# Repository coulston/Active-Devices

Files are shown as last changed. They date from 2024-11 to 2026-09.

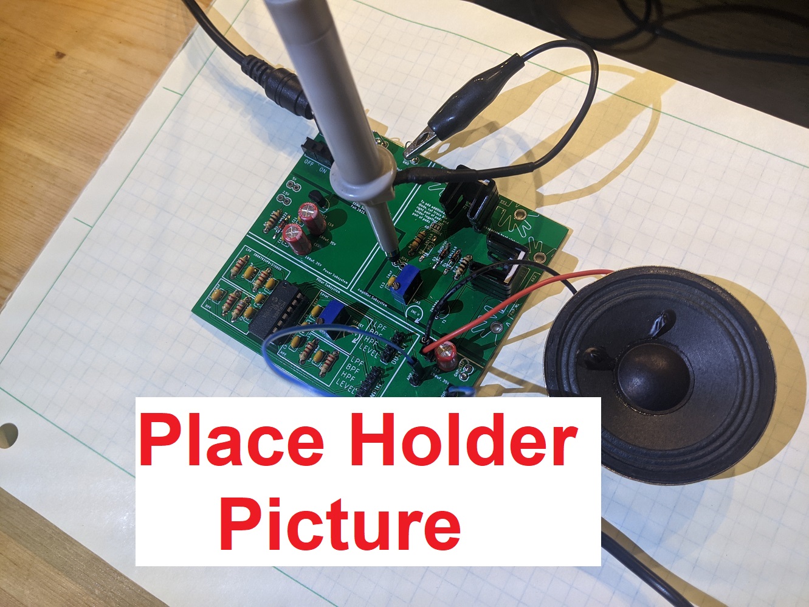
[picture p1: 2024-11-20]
Labs/lab22 audio amplifierMeasurement/img/placeHolderPicture.jpg

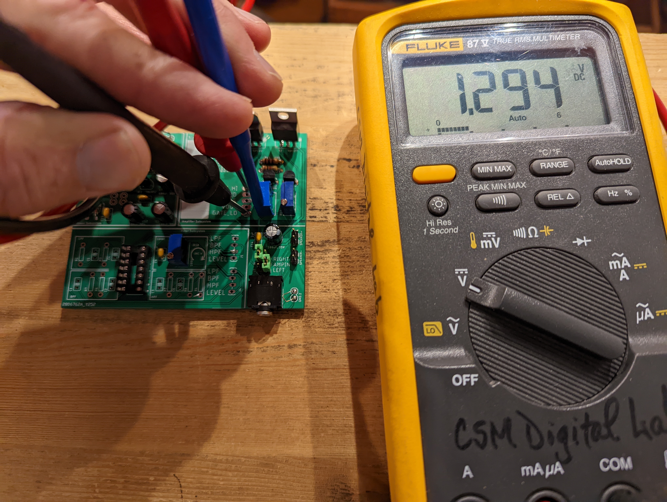
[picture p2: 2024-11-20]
Labs/lab22 audio amplifierMeasurement/img/adjustMultiplierVoltage.jpg

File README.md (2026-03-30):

Here is a set of resources that I've developed while a faculty member at the Colorado School of Mines.  These resources come in two flavors:

## Laboratories

The labs presented here require students to predict circuit behavior using circuit theory, simulate the circuit, and then build the circuit.  The first two
sets of labs below require multiple lab session to complete, showing students how combine building block circuits to produce complex behavior.
* The design/test/assembly of a BJT curve tracer on a custom PCB.  Based on w2aew's design presented on this [YouTube](https://www.youtube.com/watch?v=ZOLLoa2fH24) video.
* The design/test/assembly of an audio amplifier and audio frequency filters on a custom PCB.
* The analysis of a prebuilt, fully analog, PID controller.
* The analysis of a prebuilt full-bridge Rectifier/Buck converter.

## Workbook
I remember working problems from Schaums outline series as an undergraduate.  Working a long series of similar but distinct circuit
problems helped me hone my skill.  Most textbooks have a small set of problems to work; a volume that did not consistently produce
mastery in my students.  So I spent a summer writing the circuit problems that you will find here.  This is a work in progress and
I would certianly apprecaite any suggestions for problems to add.

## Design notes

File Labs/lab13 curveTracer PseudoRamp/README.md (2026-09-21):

# BJT Curve Tracer - Lab 4 The Pseudo Ramp Generator

This is the fourth in a series of junior year Electrical Enineering laboratories aimed at building a BJT curve tracer. 
In this lab you will analyze, simulate and assemble a Pseudo Ramp Generator that will build an almost linear ramp 
waveform with the help of the 555 Timer and Schmitt Trigger Relaxation Oscillator.  As you work you way through
the lab you will learn how to:
* Use a software tool to perform time domain analysis of an electronic circuit.
*	Analyze and design a circuit containing resistors and op amps.
*	Analyze and design a circuit consisting of several building blocks.
* Assemble a circuit on a PCB.
* Use test and measurement equipment to analyze electronic circuits.

This curve tracer is based on the YouTuber w2aew video 
[#232: More Circuit Fun: Simple transistor curve tracer using Stairstep generator circuit](https://www.youtube.com/watch?v=ZOLLoa2fH24). 
The hardware for this series of labs is located in this repo, [here](https://github.com/coulston/Active-Devices/tree/main/curveTracerResources).
Click the video below to be taken to a video overview of this laboratory.

YouTube (https://www.youtube.com/watch?v=ZmqhOJkoOfk)
  
All this material is avaible under CC BY-NC-SA 4.0

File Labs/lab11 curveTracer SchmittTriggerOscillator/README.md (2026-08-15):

# BJT Curve Tracer - Lab 2 The Schmitt Trigger Relaxation Oscillator

This is the second in a series of junior year Electrical Enineering laboratories aimed at building a BJT curve tracer. 
In this lab you will analyze, simulate and assemble a Schmitt Trigger Relaxation Oscillator that generates a low duty-cycle 
squarewave that will be an integral subsystem in the curve tracer circuit.  As you work you way through the lab you will learn how to:
* Use a software tool to perform time domain analysis of an electronic circuit.
*	Analyze and design a circuit containing resistors and op amps.
* Assemble a circuit on a PCB.
* Use test and measurement equipment to analyze electronic circuits.

This curve tracer is based on the YouTuber w2aew video 
[#232: More Circuit Fun: Simple transistor curve tracer using Stairstep generator circuit](https://www.youtube.com/watch?v=ZOLLoa2fH24). 
The hardware for this series of labs is located in this repo, [here](https://github.com/coulston/Active-Devices/tree/main/curveTracerResources).
Click the video below to be taken to a video overview of this laboratory.

YouTube (https://www.youtube.com/watch?v=oDtQ2bS_qQ8)

All this material is avaible under CC BY-NC-SA 4.0

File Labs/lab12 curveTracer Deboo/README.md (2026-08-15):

# BJT Curve Tracer - Lab 3 The Deboo Integrator

This is the third in a series of laboratories aimed at building a BJT curve tracer.  In this lab you will
analyze, simulate and assemble a circuit based on the classic 555 timer that generates a low duty-cycle
squarewave that will be an integral subsystem in the curve tracer circuit.  As you work you way through
the lab you will learn how to:
* Use a software tool to perform time domain analysis of an electronic circuit.
*	Analyze and design a circuit containing resistors and op amps.
* Assemble a circuit on a PCB.
* Use test and measurement equipment to analyze electronic circuits.

This curve tracer is based on the YouTuber w2aew video 
[#232: More Circuit Fun: Simple transistor curve tracer using Stairstep generator circuit](https://www.youtube.com/watch?v=ZOLLoa2fH24). 
The hardware for this series of labs is located in this repo, [here](https://github.com/coulston/Active-Devices/tree/main/curveTracerResources).
Click the video below to be taken to a video overview of this laboratory.

YouTube (https://www.youtube.com/watch?v=O_E52ka0kKk)

All this material is avaible under CC BY-NC-SA 4.0

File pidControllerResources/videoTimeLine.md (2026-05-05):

Overview Video

<start with graphic of PID Controller Board>

**Introduction**

For the past 10 years I've been teaching a Feedback and Control of Dynamic

Systems class at the Colorado School of Mines.  This class covers a wide variety 

of concepts and links them together.  What the class lacks is a way of creating 

a hands-on understanding of the concepts presented in class.

\*Hello, my name is Christopher Coulston and I'd like to introduce you to the 

the analog PID Controller created to address this problem.

**What is a Feedback Controller?**

In order to build a feedback controller you need something that you want to control.

We call this the plant.

<add evolving graphic, plant, ref input, error, controller>

You need to provide the feedback controller the value that you want the output to have.  This is

called the reference input.

The feedback controller computes the difference of the reference input and the plant output. This

is called the error of the system.

The error, its integral and derivative are added together creating the control signal. 

This control signal is sent as input to the plant.

The PID Controller board allows measurement of these values at a set of headers along the 

top of the board.

**Goals of the Feedback Controller**

When I started this project I had the following goals:

Physically Robust:  Students are hard on equipment and any mechanical interface is bound to break.

Inexpensive:

Made from discrete components:  I wanted student to see how simple electronic building blocks

can be assembled to form complex functionality.

Use jelly bean parts: You should be able to source the parts from many different vendors.

Flexible: Should allow users to test a variety of concepts presented in a from feedback control course.

Open Source: Please copy and adapt this work to your needs.

**The Analog PID Controller**

Let's look at the analog PID Controller.

<add graphic showing PID Controller PCB>

The headers at the top of the board provide access to all the signals in a feedback controller.

The reference input to the PID Controller comes from one of three sources:

* A push button
* A potentiometer
* An external function generator

You select the reference source by moving this jumper.

You can observe the output of the PID Controller using an oscilloscope.

The behavior of the PID Controller is determined by the PID gains, set by the three 

potentiometers.

**Using the Analog PID Controller**

Let's setup the analog PID Controller board.  This will require

* Split power supply.  A pair of 9V battery's will work fine.
* A 2-channel oscilloscope
* Optional function generator

Set up the power supply, +9V, GND and -9V

Configure and connect the function generator

Attach the output to the oscilloscope

Start tuning...

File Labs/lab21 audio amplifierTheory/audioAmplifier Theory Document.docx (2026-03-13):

EENG 385 - Electronic Devices and Circuits

Audio Board: Amplifier Theory

Lab Handout

# Outcome and Objectives

The outcome of this lab is to determine the input resistance, gain, and output resistance of the two stages in the audio amplifier. Through this process you will achieve the following learning objectives:

- Perform a DC and AC analysis of a circuit containing BJT.
- Analyze and design a circuit containing one or more BJTs.
- Analyze and design a circuit consisting of several building blocks.

# Audio Amplifier

The heart of the Audio Amplifier is shown in the schematic shown in Figure 1. In the analysis that follows, you will set VCC to 9V.

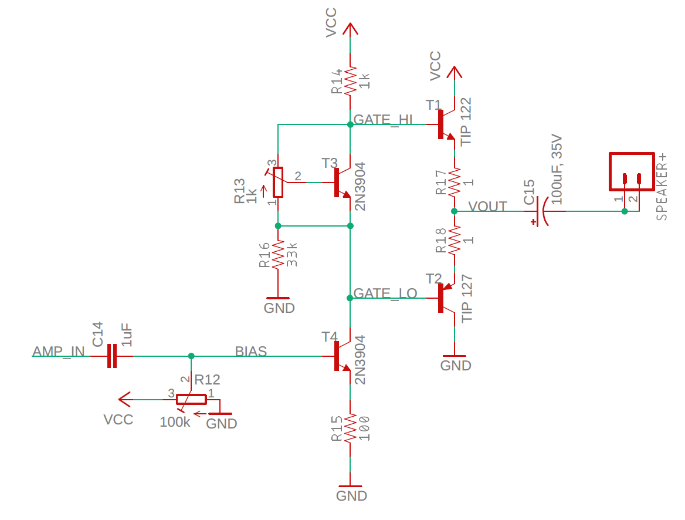
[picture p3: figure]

Figure 1: The core of the audio amplifier consists of a voltage gain stage followed by a current gain stage. Some artistic modifications have been made to the original schematic.

The output stage consists of a pair transistor/resistor pairs T1/R17 and T2/R18.

You are to treat the 1Ω resistors R17/R18, connected to the emitters of T1/T2 respectively, as 0Ω resistors. Hence, they are ignored in the rest of the following analysis. While these resistors do not play an important role in the signal amplification, these emitter degeneration resistors provide negative feedback in the output stage, helping to prevent thermal runaway.

These two output transistors are each in a common collector configuration. In the configuration shown in Figure 1:

- The base of T1 is 0.7V above the emitter.
- The base of T2 is 0.7V below the emitter

When an NPN and PNP transistor are arranged as shown in Figure 1, they are said to form a push/pull pair. The term alludes to the manner in which the pair pull the speaker towards VCC or push it towards GND. When we analyze the individual transistors in the push/pull pair, we will refer to them as emitter followers. The output of the push/pull pair should be centered at Vcc/2 = 4.5V so that the output voltage can swing as far as possible before hitting either rail.

Compute the emitter follower base voltages as follows:

1) In order for the output of the push/pull pair be 4.5V, what should you set the base voltage of transistor T1 to?
2) In order for the output of the push/pull pair be 4.5V, what should you set the base voltage of transistor T2 to?
3) What is the voltage difference between the voltages found in Questions 1 and 2?

# Common Emitter Theory

Transistor T3 in Figure 2 is configured as a common emitter. The base of T3 is the input and the collector is the output. Both the input and output voltages are measured with respect to the emitter terminal. Thus, the emitter is in common with both the base and the collector.

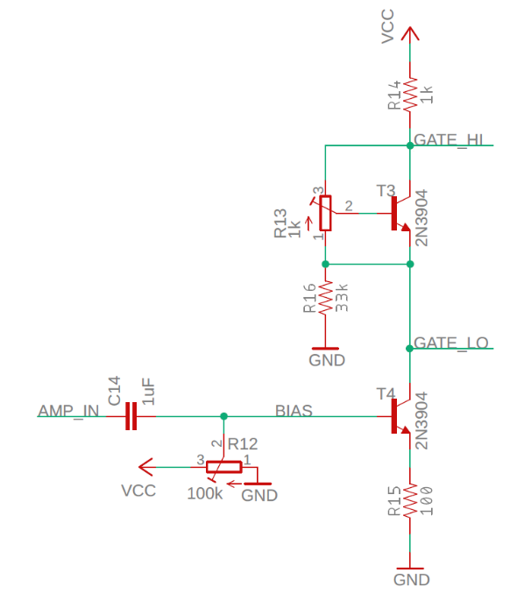
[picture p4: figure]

Figure 2: The common emitter stage of the audio amplifier.

The AMP_IN signal in Figure 2 comes from our audio source. Capacitor C14 removes the DC component from the audio signal and passes along an AC signal centered at 0V. The audio signal output of the capacitor is added (via superposition) to the bias voltage supplied by the potentiometer. You need to adjust the bias voltage so that the bases of the push/pull pair are set to the voltages you calculated in Questions 1 and 2 above. In other words, in the absence of an AC signal source, you need to:

- Set GATE_LO to 3.8V.
- Set GATE_HI to 5.2V.

Now you will use this information to adjust the bias voltage of the common emitter stage. Compute the common emitter bias voltage as follows:

1) Find the current through R14 so that GATE_HI is 5.2V where VCC = 9V.

You’ll explore the function of transistor T3 in the next section, but for the time being assume T3 is in the active mode, so IC = IE. Furthermore, assume that a negligible amount of emitter current from T3 runs through R16. Hence all the current through the resistor R14 runs into the collector of T4.

2) Find VE for T4 assuming that IE is equal to IC.
3) Find VB for T4 (your value should be close 1V).

# The Vbe Multiplier

The preceding section should have made it clear that the base of the two output transistors T1 and T2 in Figure 1 need to be 1.4V apart. This function is performed by the transistor T3, resistor R16 and the potentiometer R1 shown at left in Figure 3.

In order to make your analysis easier, ignore resistor R16. We can do this because the current flowing through R16 is 10 times smaller than the current flowing through R13. Hence, by KCL, 90% of the current flowing through R13 flows back to the emitter of T3, shown at right in Figure 3.

This circuit is called a Vbe multiplier for reasons that we will now explore.

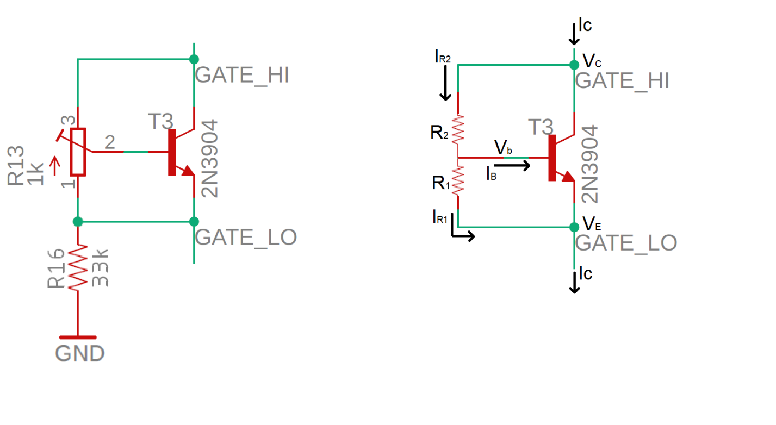
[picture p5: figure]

Figure 3: (left) The Vbe multiplier circuit used in our Audio amplifier. (right) The circuit used in the analysis.

Look at the left circuit Figure 3; adjusting the potentiometer R13 moves the center tap of the potentiometer along a 1kΩ track of resistive carbon film connecting terminals 1,3. If the center tap is moved closer to terminal 1 then the resistance between terminals 1,2 decreases and the resistance between terminals 2,3 increases. Thus, the sum of the resistance between terminals 1,2 plus the resistance between terminals 2,3 adds to 1kΩ. You will use the circuit shown in the right side of Figure 3 to analyze the Vbe multiplier. Note that the potentiometer is replaced with a pair of resistors so that R1 + R2 = 1kΩ.

1. From the previous section, what is the current IC?

Assume that the BJT in Figure 3 is in the active region and that ß = 100,

2. What is IB for this value of IC?
3. Write an equation for the current IR1 in terms of VBE and R1.
4. Assume that the center tap of the potentiometer is halfway so that R1 = R2 and VBE = 0.7V. What is the current IR1 equal to?
5. In this case, how much larger is IR1 than IB? Compute this as the ratio IR1/IB.
6. Write a KCL equation for the VB node.
7. Since IR1 is a lot larger than IB, rewrite this KCL assuming that IB = 0.
8. Write an equation for VCB in terms of IR2 and R2.
9. Replace the IR2 term in the previous step with the equation in step 3
10. Write an equation for VCE in terms of VCB and VBE.
11. Replace the VCB term in the previous step using the equation in part 9
12. Factor out the VBE term in the previous step.

This final equation shows that VCE is VBE times some factor. In other words, VBE is multiplied by a factor to get VCE. Hence the name, Vbe multiplier.

Now let’s dig into the amplifier using the framework shown in Figure 4. This figure is an abstract version of Figure 1 for small AC signals. It describes how the signal is mathematically manipulated. The Source is the audio input that you are providing.

The blue area labeled Common Emitter in Figure 4 is the circuit shown in Figure 2. Let’s look at this stage in the overall circuit shown in Figure 1. The input to this stage, Vce is the voltage at the base of transistor T4 in Figure 1, the BIAS test point on the PCB. The output of the Common Emitter stage is the collector of transistor T4 in Figure 1, the GATE_LO test point.

The blue area labeled Emitter Follower in Figure 4 is the circuit shown in Figure 6. Let’s look at this stage in the overall circuit shown in Figure 1. The input to this stage, Vef, is the voltage at the base of transistor T2 in Figure 1, the GATE_LO test point. The output from this stage is the emitter of transistor T2 in Figure 1, the VOUT test point.

Some of you may have wondered why include resistor R16 at all? R16 is included in Figure 2 so that there is always a path for current to flow through the biasing potentiometer R13 regardless what the amplifier is doing.

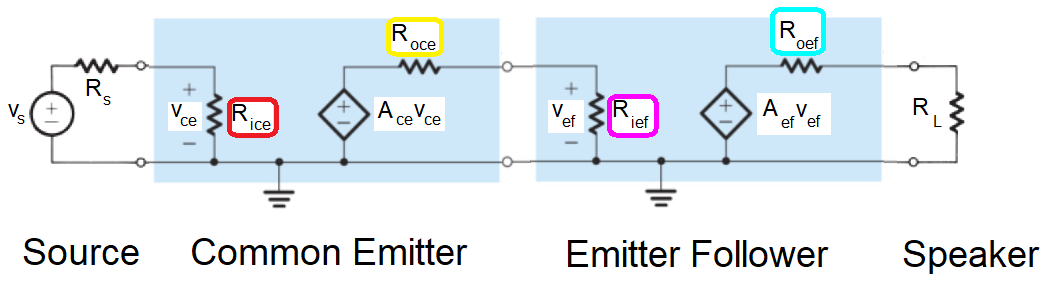
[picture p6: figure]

Figure 4: The small signal model of the Audio board. The input signal goes through a common emitter to amplify the voltage and then into an emitter follower to amplify the current before being sent out to the speakers.

Your task is to assign equations and values to the variables in Figure 4 and put them into Table 1. This information is critical in understanding how to improve the quality of the audio output.

Table 1: Model parameters for the cascade amplifier shown in Figure 4.

| Rin | Rout | Voltage Gain
Source | N/A | Rs = 10Ω | N/A
Common Emitter | Rice = | Roce = | Ace =
Emitter Follower | Rief = | Roef = | Aef =
Speaker | RL = 8Ω

Let’s start by analyzing the common emitter amplifier from Figure 2, but in the more reduced form shown in Figure 5. Note the Vbe multiplier has been remove from Figure 2 and replaced by a wire. This is an acceptable substitution because we are interested in the behavior of the common emitter BJT, not the Vbe multiplier.

In this analysis you are frequently going to be asked to find the change in voltage of a node. A change in a voltage is not the same thing as the value of the voltage. For example, if I asked you to describe the relationship between the change in the emitter voltage (ΔVE ) in Figure 5 and the change in emitter current (ΔIE), you could use Ohm’s law to write:

ΔVE = R ΔIE

If you were then asked to solve this equation for ΔIE, you would write:

ΔIE = ΔVE/R

The steps in the derivations are numbers. Occasionally you will need to use an equation derived in a previous step to move the derivation forwards. When doing this, look for equivalent variables in the two steps, you will probably either substitute one equation into another or set two equations equal.

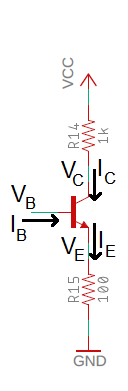
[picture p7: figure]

Figure 5: A simplified version of the common emitter shown in Figure 2.

Compute the input impedance of the common emitter stage - Rice. You will need to reference Figure 5 during this analysis.

1) What is the relationship between ΔVB and ΔVE?
2) Use Ohm’s law to describe the relationship between ΔVE and ΔIE.
3) Solve the previous equation for ΔIE and replace ΔVE with ΔVB from step 1.
4) Write down the relationship between ΔIE and ΔIB? (Hint, it is a bad parameter.)
5) Equate the equations from step 3 and 4 using ΔIE.
6) Solve equation from step 5 for ΔVB / ΔIB, this is the input impedance of the common emitter. Insert this value into the Rice cell of Table 1.

Compute the output impedance of the common emitter stage - Roce. You will need to reference Figure 5 during this analysis.

1) Use Ohm’s law to describe the relationship between ΔVC and ΔIC.
2) Solve Equation 1 for ΔVC/ΔIC. This value is the output impedance of the common emitter. Insert this value into the Roce cell of Table 1.

Compute the gain of the common emitter stage - Ace. You will need to reference Figure 2 during this analysis.

1) What is the relationship between ΔVB and ΔVE?
2) Use Ohm’s law to describe the relationship between ΔVE and ΔIE.
3) Solve the previous equation for ΔIE.
4) Replace ΔVE in the equation from step 3 with the relationship found in the equation from step 1.
5) Use Ohm’s law to describe the relationship between ΔVC and ΔIC. Note the sign!
6) Since ΔIE = ΔIC, replace ΔIC in the previous step with ΔIE.
7) Substitute ΔIE from the equation in step 4 into the equation from step 6.
8) Let ΔVC/ΔVB, be the gain. What is the gain of our amplifier? Insert this value into the Ace cell of Table 1.

# Emitter Follower Theory

We now return our attention to the cascade amplifier of Figure 4 and fill in the Table 1. We will focus on the push/pull output stage formed by a pair of emitter followers. I’ve made some changes to the push/pull circuit shown in Figure 1 to produce the circuit shown in Figure 6.

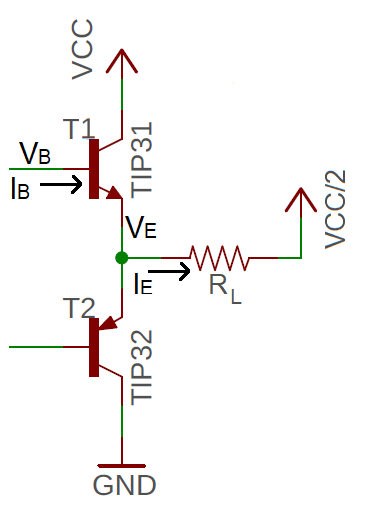
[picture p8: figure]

Figure 6: The output stage of the audio amplifier consists of a pair of emitter followers.

I made the changes going from Figure 1 to Figure 6. These changes are valid and made to simplify the analysis. For example, since this is a small signal analysis (we are looking at changes in values e.g. ΔVB) we will ignore the 100uF capacitor C13 in Figure 6 because the capacitor appears as a short at audio-frequencies. The speaker is rated as an 8Ω load, represented by RL – please use RL in the subsequent analysis. Finally, focus on the labeled NPN transistor, T1, in Figure 6 when answering the following questions.

Compute the input impedance of the emitter follower - Rief. You will need to reference Figure 6 during this analysis.

1) What is the relationship between ΔVB and ΔVE?
2) Use Ohm’s law to describe the relationship between ΔVE and ΔIE. Call the resistance of the speaker RL.
3) Solve the previous equation for ΔIE and replace ΔVE with ΔVB (using the relationship in equation 1)
4) What is the relationship between ΔIE and ΔIB? Hint, it involves a bad parameter.
5) Equate the equations from steps 3 and 4 using ΔIE.
6) Solve equation in step 5 for ΔVB/ΔIB, this is the input impedance of the emitter follower. Insert this value into the Rief cell of Table 1.

Compute the output impedance of the emitter follower – Roef. You will need to reference Figure 6 during this analysis.

1) Use Ohm’s law to describe the relationship between ΔVE and ΔIE. Call the resistance of the speaker RL.
2) Solve the equation from step 1 for ΔVE/ΔIE, this is the output impedance of the emitter follower. Insert this value into the Roef cell of Table 1.

Compute the voltage gain of the emitter follower - Aef. You will need to reference Figure 6 during this analysis.

1) What is the relationship between ΔVB and ΔVE?
2) Solve the equation from step 1 for ΔVE/ΔVB, this is the voltage gain of the emitter follower. Insert this value into the Aef cell of Table 1.

Compute the overall gain of amplifier with no load:

Since our analysis will break down if we do not have a load resistance, we will model an open circuit output as a 1MΩ resistor as shown in Figure 7. In this analysis assume a value of β =100.

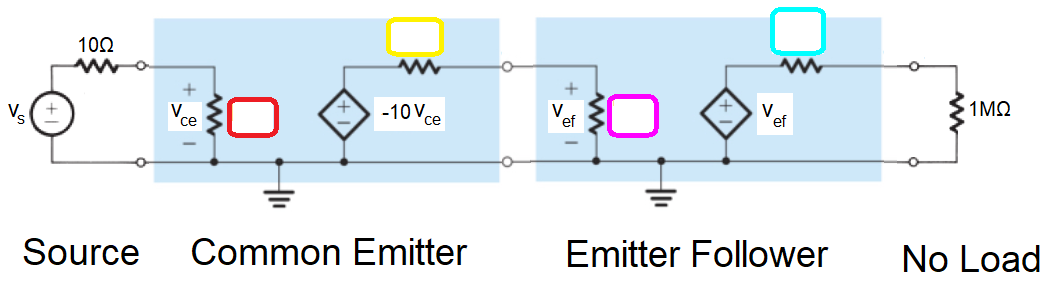
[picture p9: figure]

Figure 7: The Audio amplifier with a very high load resistance that models no load.

1. Fill in the values of the resistors shown in Figure 7.
2. Compute Vce in terms of Vs. Use this to determine the gain Vce/Vs. Assume 20,000 + 10 = 20,0000.
3. Compute Vef in terms of Vs. Use this to determine the gain Vef/Vs. Assume 200,000,000 +1,000 = 200,000,000
4. Calculate the current delivered to the 1MΩ load. Assume that 1/1,000,000 = 0.

Analysis of amplifier with 8Ω load

We will model the speaker as an 8Ω resistor as shown in Figure 7. In this analysis assume a value of β =100.

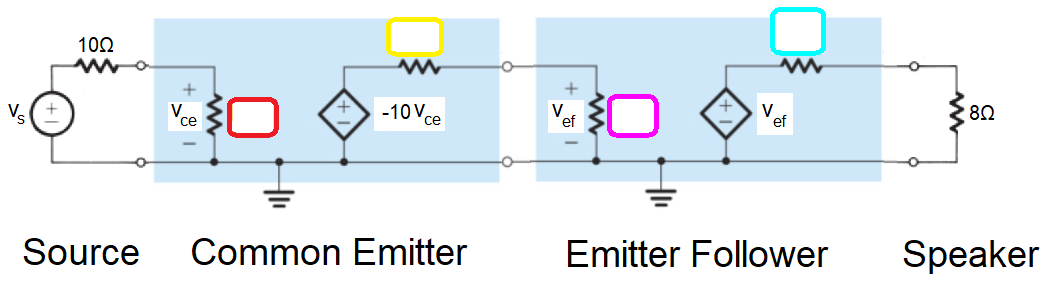
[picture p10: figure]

Figure 8: The Audio amplifier with an 8Ω load that represents a speaker.

1. Fill in the values of the resistors shown in Figure 8. Assume β =100.
2. Compute Vce in terms of Vs. Use this to determine the gain Vce/Vs. Assume 20,000 + 10 = 20,000.
3. Compute Vef in terms of Vs. Use this to determine the gain Vef/Vs.
4. Calculate the current delivered to the 8Ω load in terms of Vs.

# Assembly

This lab document does not contain any information of the assembly process. Please consult the Assembly Guide posted on Canvas for more information.

# Testing the Amplifier Subsystem

Until the pair of potentiometers are adjusted, your amplifier subsystem will not work properly. It would be best to have someone else check your component placement and orientations and check theirs. Then come to lab next week ready to learn how to adjust the potentiometers and get some sound from your amplifier.

# Turn In

Make a record of your response to numbered items below and turn them in a single copy as your team’s solution on Canvas using the instructions posted there. Include the names of both team members at the top of your solutions. Use complete English sentences to introduce what each of the following listed items (below) is and how it was derived.

Hint, use Ctrl+click to follow links. This also works for all the Figures and Tables in these labs.

Audio Amplifier

Steps 1 – 3

Common Emitter Theory

Steps 1 – 3

The Vbe Multiplier

Steps 1 – 12

Compute the input impedance of the common emitter stage - Rice.

Steps 1 – 6

Compute the output impedance of the common emitter stage - Roce.

Steps 1 – 2

Compute the gain of the common emitter stage - Ace.

Steps 1 – 8

Compute the input impedance of the emitter follower - Rief.

Steps 1 – 6

Compute the output impedance of the emitter follower – Roef.

Steps 1 – 2

Compute the voltage gain of the emitter follower - Aef.

Steps 1 – 2

Compute the overall gain of amplifier with no load

Steps 1 – 4

Compute the overall gain of amplifier with 8Ω load

Steps 1 – 4

Complete Table 1

Audio Board: Amplifier Theory

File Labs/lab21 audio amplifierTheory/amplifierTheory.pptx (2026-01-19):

## EENG 385 Amplifier Theory

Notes: Usually the <title of the lab> is what will be called the “System” through the rest of this document

## Lab Objectives

The objective of this lab is to analyze the operation and electrical characteristics of the audio amplifier stage of the Audio board and to prepare you to solder together the audio amplifier subsystem of the Audio board.

## Theory

Two stage
- Input from audio source via 3.5mm jack
- Common emitter, voltage amplifier
- Emitter follower, current amplifier

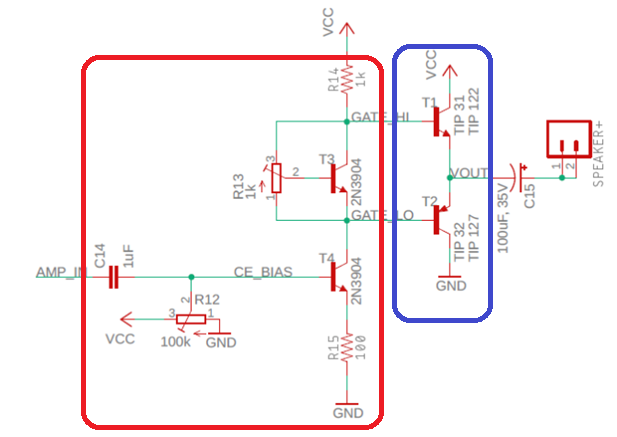
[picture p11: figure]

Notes: Replace <System> with the name of the

## Theory

- Model circuit with small signal model
- Vs is audio source, your MP3 player
- Use analysis to determine values in colored boxes


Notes: Replace <System> with the name of the

## Small Signal Input Resistance

- Small signal input resistance
  - Looks at changes in voltage/current
- Example: Find Rice
  - V = I*R so Rice = ΔvB / ΔiB
  - Effect of ΔvB on ΔvE at T4?
  - Effect of ΔiE on ΔvE at T4?
  - Relationship between ΔiB on ΔiE

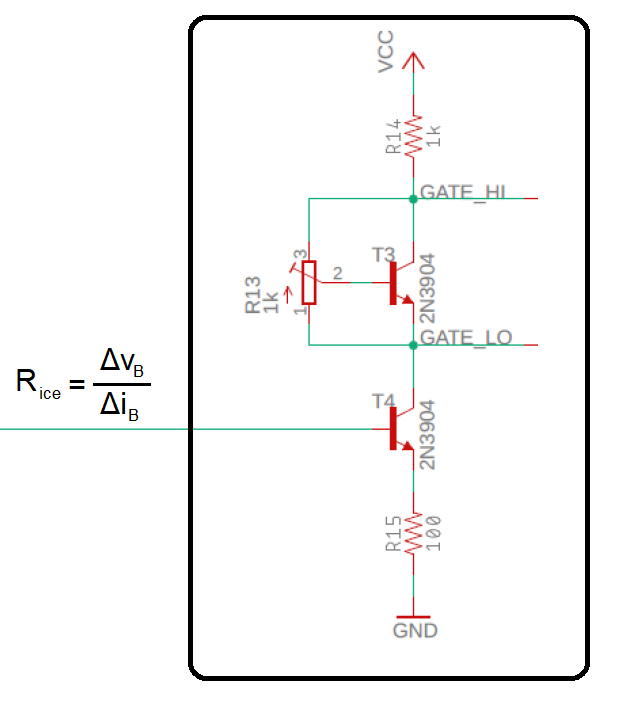
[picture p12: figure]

## Assemble

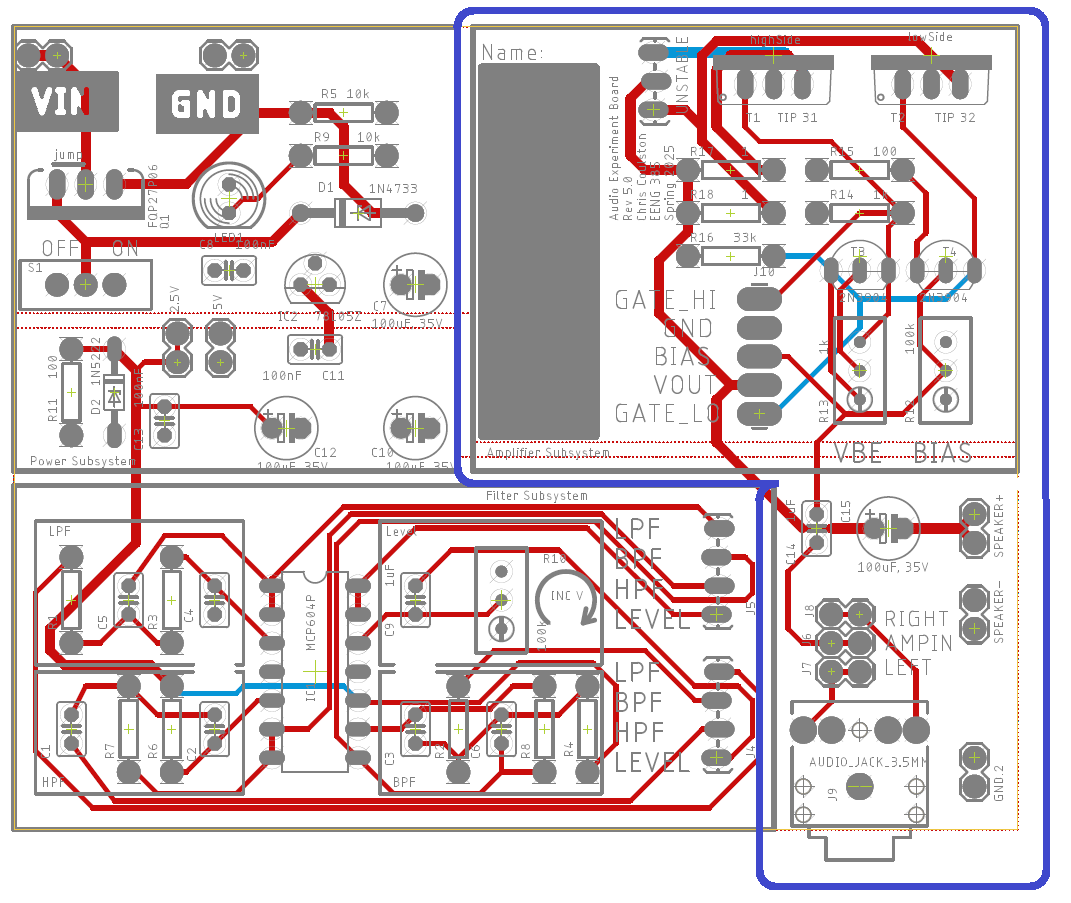
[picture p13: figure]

- Audio input & amplifier
- Polarized parts
  - 100uF
  - TIP 122 NPN
  - TIP 127 PNP
  - 2N3904
  - 1k and 100k Pot

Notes: Replace <System> with the name of the

## Test

- No testing of assembled circuit
  - If POTs are not adjusted, it may look like your circuit has a short circuit
  - Wait until next week’s lab to power up.

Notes: Replace <System> with the name of the

## Turn In

Audio Amplifier Steps 1 – 3
Common Emitter Theory Steps 1 – 3
The Vbe Multiplier Steps 1 – 12
Rice Steps 1 – 6
Roce Steps 1 – 2
Ace Steps 1 – 8
Rief Steps 1 – 6
Roef Steps 1 – 2
Aef Steps 1 – 2
Gain of amplifier with no load Steps 1 – 4
Gain of amplifier with 8Ω load Steps 1 – 4
Complete Table 1

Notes: Replace <System> with the name of the

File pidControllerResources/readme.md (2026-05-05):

# PID Controller

<image of PID Controller>

The PID Controller board is designed as a practical laboratory experience for students to understand how to characterize a plant, and tune a PID Controller.  Through this process you will achieve the following learning objectives:
* Analyze an opamp circuit that implements a PID controller and plant.
* Characterize a plant
  * Determine the transfer function of the plant
  * Determine the frequency reponse of the plant by building its Bode plot
  * Compute gain and phase margin of a plant by building its Nyquist plot
* Hands on tuning of a PID controller.

Video Title (https://www.youtube.com/watch?v=VIDEO_ID)

# Documentation
* [PID Laboratory](../Labs/lab50%20pidController/pidControllerLab.pdf)
* Videos
    * Overview
    * Characterizing the plant
* Hardware
    * PID Controller [Schematic](./pidControllerRev8schematic.pdf) and [Layout](./pidControllerRev8layout.pdf)
    * Source files to build your own
       * EAGLE CAD [Schematic](./manufacture/pidControllerRev8.sch) and [Layout](./manufacture/pidControllerRev8.brd)
       * [Gerber Files](./manufacture/pidControlRev8Gerber)
       * [Bill of Materials](./manufacture/pidControllerMaster_BOM.xlsx)
       * [Centroid File](./manufacture/pidController_Centroid.xlsx)

# Respository Contents

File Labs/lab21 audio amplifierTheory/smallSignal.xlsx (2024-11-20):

gm | 0.1181102362
 |  | Measure |  |  | Calculated
Freq | Volume Setting | Vb(ch1)pp | Ve(ch2)pp | Vc(pp) | Vbe(pp) | ic(pp) mA | Vc(pp) error
1kHz | 30 | 200 | 181 | 1.8 | 19 | 2.24 | 0.44
 | 40 | 265 | 240 | 2.4 | 25 | 2.95 | 0.55
 | 50 | 330 | 298 | 3 | 32 | 3.78 | 0.78
 | 60 | 393 | 355 | 3.5 | 38 | 4.49 | 0.99
 | 70 | 458 | 414 | 4.05 | 44 | 5.2 | 1.15
 | 80 | 523 | 469 | 4.59 | 54 | 6.38 | 1.79
 | 90 | 589 | 524 | 5.12 | 65 | 7.68 | 2.56
 | 100 | 652 | 572 | 5.56 | 80 | 9.45 | 3.89

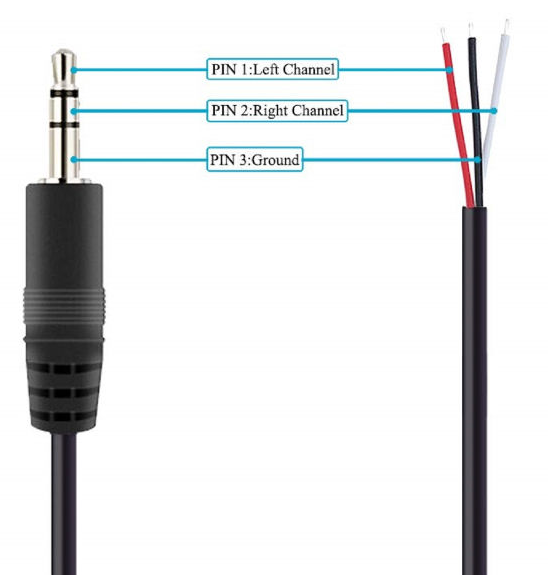
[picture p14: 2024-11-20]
Labs/lab21 audio amplifierTheory/img/audioCable.bmp

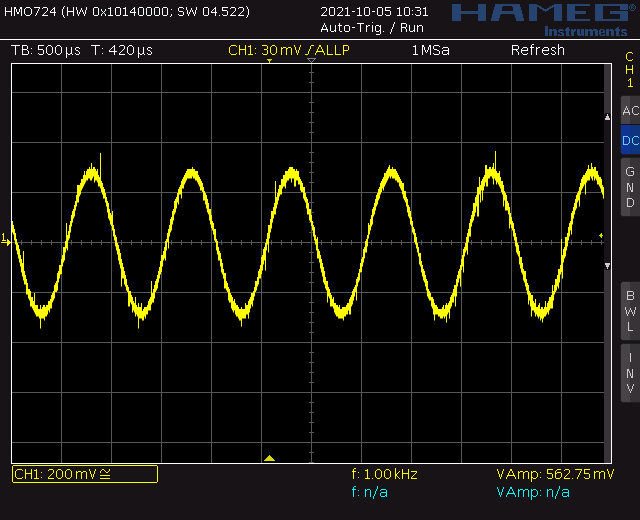
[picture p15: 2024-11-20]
Labs/lab21 audio amplifierTheory/img/audioInput.PNG

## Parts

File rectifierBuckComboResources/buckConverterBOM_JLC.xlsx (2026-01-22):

Comment | Designator | Footprint | JLCPCB Part #（optional）
5.08mm 1 2 Through Hole | V_AC | P=5.08mm | C8465
ERR1HM101F09OT | C1 | SANYO-OSCON_F | C433177
ERR1HM101F09OT | C2 | SANYO-OSCON_C | C3035369
 | R1,R2 | AXIAL-0.3 | C2903232
MF1/4W-10K±1%-ST52 | R3 | AXIAL-0.3 | C2903245
RES 470Ω ±5% 1W Through Hole,D2.4xL6.3mm | R5 | Through Hole,D2.4xL6.3mm | C1741176
MF3WS-100Ω±1%T | R4 | 0414/15 | C714177
VLU0810-102K | L1 | 10mmx12mm | C72626
LED YELLOW GREEN FROSTED GREEN LENS TH | D1 | 5mm | C99697
1N4004-E3/54 | D2,D3,D4,D5 | DO41 | C511070
1N5819 | D6 | DO41 | C110032
2N7000 | Q1 | TO-92-2.54mm | C107290
FQP30N06L-VB | Q2 | TO220AB | C2575
SWITCH SLIDE SP3T TH | S2 | Custom | C221831
SWITCH SLIDE SPDT TH | S1,S3 | Custom | C221829
2N3906 | T1 | TO-92 | C258186
2N3904 | T2 | TO-92 | C258184
J1 | J1 | 3pin header | C2937625
Aligator Connector | PWM,VSS.0,VSS.1 | Custom | C238129

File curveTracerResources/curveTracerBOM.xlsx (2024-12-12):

DigiKey Order
Description | Manf | Manf Part # | DigiKey Part # | Unit Cost | Per Qty | Per Student
100 OHM 5% 1/4W AXIAL | Stackpole Electronics Inc |  |  | $0.01 | 1 | $0.01
1.0 kOhms ±5% 0.25W, 1/4W Through Hole Resistor Axial Flame Retardant Coating, Safety Carbon Film | Stackpole Electronics Inc |  |  | $0.01 | 4 | $0.06
10K OHM 5% 1/4W AXIAL | Stackpole Electronics Inc | CF14JT10K0 | CF14JT10K0CT-ND | $0.01 | 12 | $0.18
100 kOhms ±5% 0.5W, 1/2W Through Hole Resistor Axial Flame Retardant Coating, Safety Carbon Film | Stackpole Electronics Inc | CF12JT100K | CF12JT100KCT-ND | $0.01 | 5 | $0.07
CAP CER 10nF 100V X7R RADIAL | KEMET | C315C103K1R5TA7303 | 399-13907-1-ND | $0.10 | 2 | $0.20
CAP CER 0.1UF 50V X7R RADIAL | Vishay Beyschlag/Draloric/BC Components | K104K10X7RF5UH5 | BC2665CT-ND | $0.09 | 5 | $0.45
CAP ALUM 100UF 20% 35V RADIAL | Würth Elektronik | #860010573007 | 732-8737-1-ND | $0.10 | 1 | $0.10
CONN PWR JACK 2X5.5MM KINKED PIN | CUI Devices | PJ-202A | CP-202A-ND | $0.43 | 1 | $0.43
Slide Switch SPDT Through Hole | E-Switch | EG1218 | EG1903-ND | $0.61 | 1 | $0.61
3 Position Header Connector 0.100" (2.54mm) Through Hole Gold | Sullins Connector Solutions | PPPC031LFBN-RC | S7036-ND | $0.27 | 1 | $0.27
14-pin Socket |  |  |  |  | 1
8-pin Socket |  |  |  |  | 1
555 Type, Timer/Oscillator (Single) IC 100kHz 8-PDIP | Texas Instruments | NE555P | 296-NE555P-ND | $0.40 | 1 | $0.40
J-FET Amplifier 4 Circuit - 14-PDIP | Texas Instruments | TL074CN | 296-1777-ND | $0.84 | 1 | $1.80
Green 572nm LED Indication - Discrete 2.1V Radial | Würth Elektronik | 151051VS04000 | 732-5017-ND | $0.20 | 1 | $0.20
Diode Standard 100 V 200mA Through Hole DO-35 | onsemi | 1N4148 | 1N4148FS-ND | $0.10 | 6 | $0.30
Bipolar (BJT) Transistor PNP 40 V 200 mA 250MHz 625 mW Through Hole TO-92 | NTE Electronics, Inc | 2N3906 | 2368-2N3906-ND | $0.11 | 2
2N7000 |  |  |  |  | 4
3M VIRTUA PROTECTIVE EYE 1=1PC | 3M | 11228-00000-100 | 3M158306-ND | $0.86 | 1 | $0.86
 |  |  |  |  |  | $5.94

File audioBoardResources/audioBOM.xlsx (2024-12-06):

DigiKey Order
Description | Manf | Manf Part # | DigiKey Part # | Foot | Unit Cost | Per Qty | Per Student
100 Ohms ±5% 0.25W, 1/4W Through Hole Resistor Axial Flame Retardant Coating, Safety Carbon Film | Stackpole Electronics Inc | CF14JT100R | CF14JT100RCT-ND |  | $0.01 | 2 | $0.02
RES 1K OHM 5% 1/4W AXIAL | Stackpole Electronics Inc | CF14JT1K00 | CF14JT1K00CT-ND |  | $0.01 | 1 | $0.01
RES 10K OHM 5% 1/4W AXIAL | Stackpole Electronics Inc | CF14JT10K0 | CF14JT10K0CT-ND |  | $0.01 | 2 | $0.03
100 kOhms 0.5W, 1/2W PC Pins Through Hole Trimmer Potentiometer Cermet 18.0 Turn Top Adjustment | Nidec Copal Electronics | CT94EW104 | CT94EW104-ND |  | $1.55 | 3 | $4.65
CAP ALUM 100UF 20% 35V RADIAL | Würth Elektronik | #860010573007 | 732-8737-1-ND |  | $0.10 | 4 | $0.41
0.1uF | Vishay Beyschlag/Draloric/BC Components | K104K10X7RF5UH5 | BC2665CT-ND |  | $0.10 | 3
1uF |  |  |  |  |  | 2
CONN HEADER VERT 6POS 2.54MM | Harwin Inc. | M20-9980346 | 952-2121-ND |  | $0.29 | 1 | $0.29
Slide Switch SPDT Through Hole | E-Switch | EG1218 | EG1903-ND |  | $0.68 | 1 | $0.68
3.50mm (0.141", 1/8", Mini Plug) - Headphone Phone Jack Stereo (3 Conductor, TRS) Connector Solder | CUI Devices | SJ1-3525N | CP1-3525N-ND |  | $0.76 | 1 | $0.76
Heat Sink TO-220 Aluminum 3.0W @ 60°C Board Level | Assmann WSW Components | V8508G | A10755-ND |  | $0.31 | 2 | $0.62
14 (2 x 7) Pos DIP, 0.3" (7.62mm) Row Spacing Socket Tin Through Hole | Assmann WSW Components | A 14-LC-TT | AE9989-ND |  | $0.23 | 1 | $0.23
Zener Diode 5.1 V 1 W ±5% Through Hole DO-41 | onsemi | 1N4733ATR | 1N4733AFSCT-ND |  | $0.05 | 1 | $0.05
DIODE ZENER 2.5V 500MW DO35 | onsemi | 1N5222B | 1N5222B-ND |  | $0.16 | 1 | $0.16
Green 572nm LED Indication - Discrete 2.1V Radial | Würth Elektronik | 151051VS04000 | 732-5017-ND |  | $0.20 | 1 | $0.20
Linear Voltage Regulator IC Positive Fixed 1 Output 100mA TO-92-3 | STMicroelectronics | L78L05CZ | 497-7268-ND |  | $0.51 | 1 | $0.51
Bipolar (BJT) Transistor NPN 40 V 200 mA 300MHz 625 mW Through Hole TO-92 | NTE Electronics, Inc | 2N3904 | 2368-2N3904-ND |  | $0.11 | 1 | $0.11
Bipolar (BJT) Transistor NPN - Darlington 100 V 5 A 2 W Through Hole TO-220 | STMicroelectronics | TIP122 | 497-2543-5-ND |  | $0.82 | 1
Bipolar (BJT) Transistor PNP - Darlington 100 V 5 A 2 W Through Hole TO-220 | STMicroelectronics | TIP127 | 497-2571-5-ND |  | $0.79 | 1
General Purpose Amplifier Circuit Rail-to-Rail 14-PDIP | Microchip Technology | MCP6004-I/P | MCP6004-I/P-ND |  | $0.51 | 1 | $0.51
P-Channel 60 V 27A (Tc) 120W (Tc) Through Hole TO-220-3 | onsemi | FQP27P06 | FQP27P06-ND |  | $2.21 | 1 | $2.21

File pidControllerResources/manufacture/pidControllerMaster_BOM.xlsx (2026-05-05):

Comment | Designator | Footprint | Butter | Bessel | Cheby -3dB
100uF, 35V | C1 | SANYO-OSCON_C | C47891
CAP CER 10nF 50V X7R 1206 | C2, C11, C12 | C1206 | C1846
CAP CER 1uF 50V X7R 1206 | C3, C4 | C1206 | C90539
CAP CER 33nF 50V X7R 1206 | C9 | C1206 | C1864
1N4148 | D1, D2 | SOD-323 | C60580
14P DIP 7.62mm 2.54mm DIP-14 IC Sockets RoHS | IC1, IC2, IC3, IC4 | DIL14 | C2325
CONN HEADER 6POS 2.54mm DUAL ROW TH | J4 | 2X3 | C492420
CONN HEADER 2POS 2.54mm SINGLE ROW TH | PLANT_IN, PLANT_OUT | 1x2 | C492401
LED EMERALD GREEN WATER CLEAR 1206 SMD | LED1 | D1206 | C965825
2N7000 | Q1 | TO-92-2.54mm | C107290
POT 50kΩ 500mW Through Hole | R1, R26 | Through Hole-3P,7x6.8mm | C48997904
RES 1kΩ ±1% 250mW 1206 | R12, R15, R16, R17, R18, R19, R20, R21, R22, R27, R28, R29, R34 | R1206 | C4410
15k | R1_1 | R1206 | C25828 | C17902 | C25834
22k | R2_1 | R1206 | C25830 | C25828 | C17900
100nF | C1_1 | C1206 | C110253 | C110253 | C110253
68nF | C2_1 | C1206 | C1880 | C1880 | C1856
22k | R1_2 | R1206 | C25830 | C17902 | C17916
100k | R2_2 | R1206 | C17900 | C25836 | C17929
100nF | C1_2 | C1206 | C110253 | C110253 | C110253
10nF | C2_2 | C1206 | C1846 | C1864 | C1881
RES 10kΩ ±1% 250mW 1206 | R2, R8, R9, R10, R11, R30, R33, R36, R37 | R1206 | C17902
RES 3.3kΩ ±1% 250mW 1206 | R24 | R1206 | C26032
RES 22kΩ ±1% 250mW 1206 | R3 | R1206 | C25830
RES 100Ω ±1% 250mW 1206 | R31 | R1206 | C17901
RES 100kΩ ±1% 250mW 1206 | R32 | R1206 | C17900
POT 100kΩ Through Hole-3P,9.5x4.9mm Slide Potentiometers RoHS | R35 | Through Hole-3P,9.5x4.9mm | C48997936
RES 6.8kΩ ±1% 250mW 1206 | R4 | R1206 | C26034
POT 10kΩ Through Hole | R5, R6, R7 | EVUF | C209779
SMD-4P,6x6mm Tactile Switches RoHS | S1 | SMD-4P,5.1x5.1mm | C318884
SWITCH SLIDE DPDT SMD | S2 | AYZ0202 | C2906280
2N3906 | T1, T2 | TO-92-3 | C124483
Aligator Connector | FNC,GND.0,GND.1,GND.2,VCC,VSS | Custom | C238129

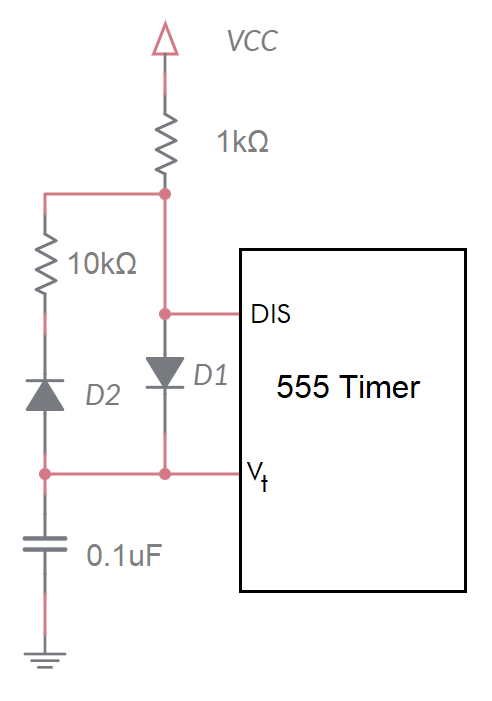
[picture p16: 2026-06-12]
Labs/lab10 curveTracer 555timer/img/External Parts on 555-timer.bmp

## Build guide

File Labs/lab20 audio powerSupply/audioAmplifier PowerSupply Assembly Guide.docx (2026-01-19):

EENG 385 - Electronic Devices and Circuits

Audio Board: Power Supply

Assembly Guide

# Soldering Together the Power Subsystem

The Audio board has far fewer resistors than the BJT curve tracer. Even so, it is worth your time to brush-up on how to interpret the resistors color bands of the resistors to be used in this lab.

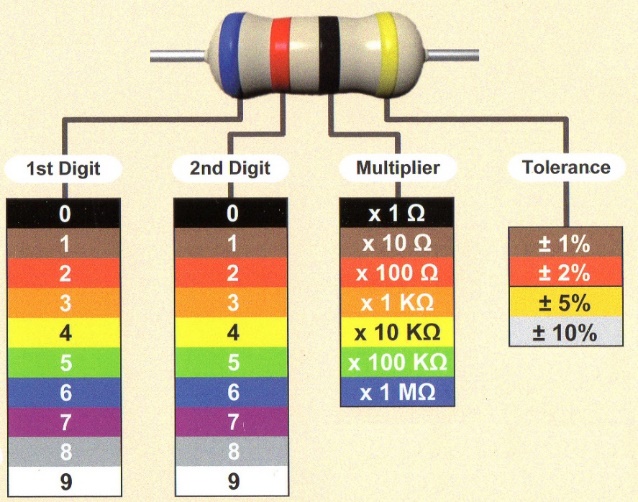
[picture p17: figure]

Figure 1: The colored bands on resistors encode its resistance.

You will be soldering the power subsystem for the Audio board this week using the schematic in Figure 2. On a philosophical note, the schematic shows the logical relationship between parts in a familiar format. When I design a schematic, I try to isolate function units of the design. Then, I connect these functional units together using named wires. Named wires greatly reduce the wiring clutter on the schematic and make the schematic more readable.

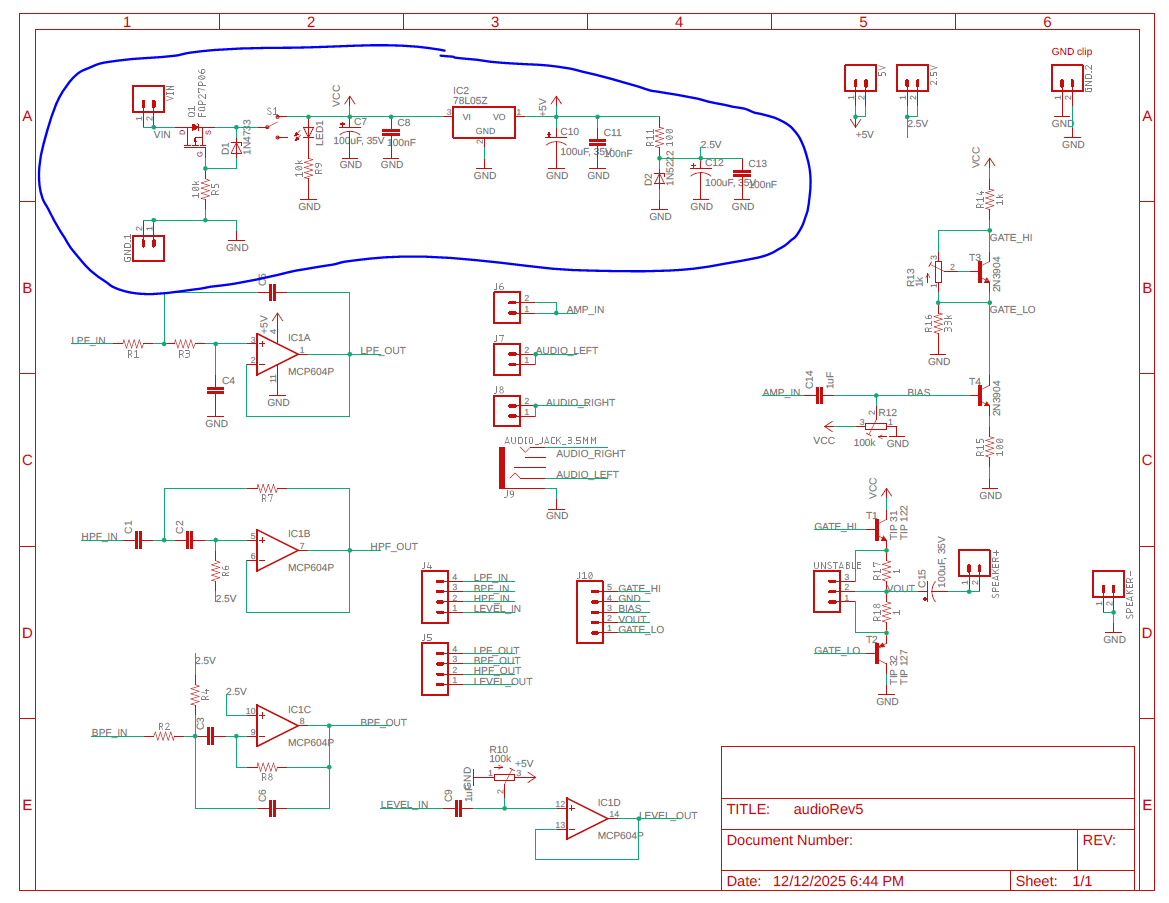
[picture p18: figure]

Figure 2: The schematic for the Audio board with the power subsystem circled in blue.

Like, your previous experiences, the parts in this schematic have a designator and a value. These designators are used to relate a part in the schematic with the layout. I converted the schematic in Figure 2 to the layout shown in Figure 3. As before, the physical position of the parts in the schematic and layout are unrelated, the schematic is an abstraction of the finished layout. The layout contains all the data used in the fabrication of the PCBs – the layout and the fabricated PCB are identical.

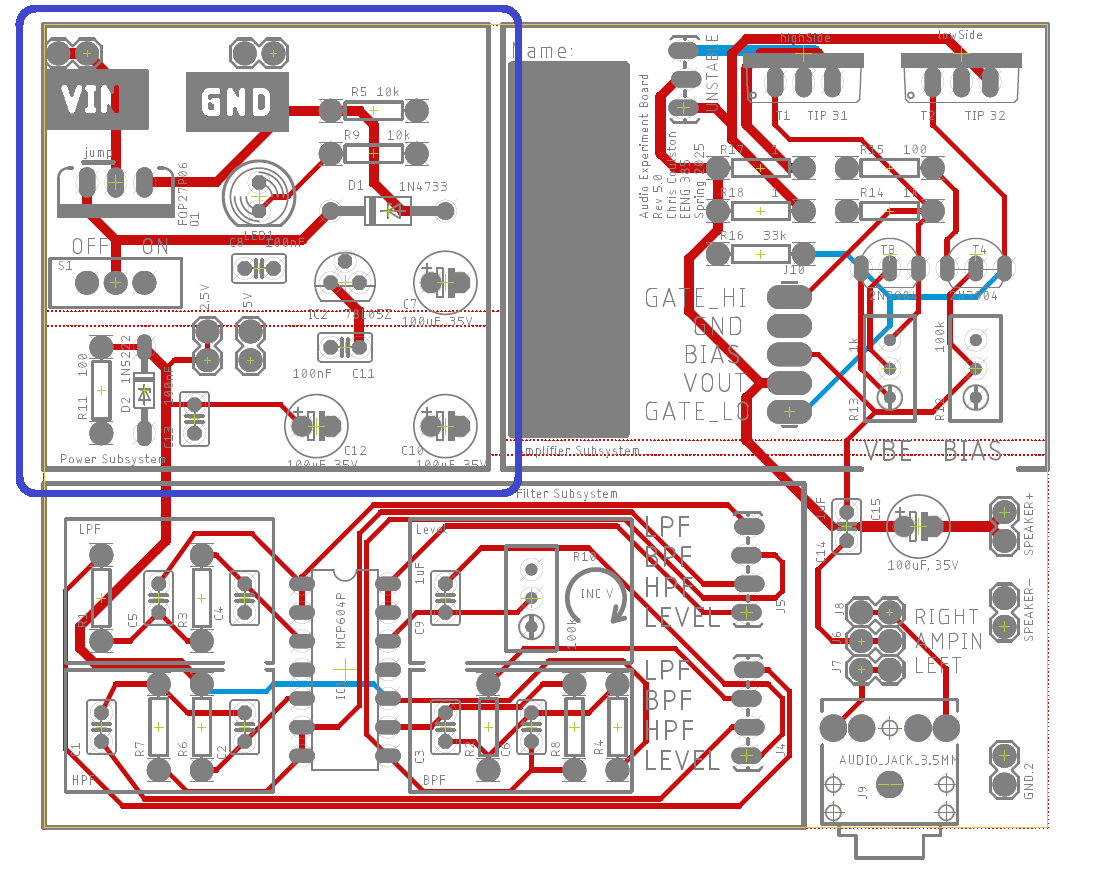
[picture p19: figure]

Figure 3: The layout of the Audio board with the power subsystem outlined in blue.

You should notice parts logically related in the schematic are physically proximal in the layout.

# Polarized Parts

Most of the parts to be soldered into the PCB can be installed in more than one way. Parts which must be installed in a correct orientation are called polarized. Polarized parts have some physical indication of their orientation and the silk screen will have some markings to show you where this physical indicator should be aligned. Let’s walk through all the polarized parts that you will solder this week and how you will install them in the PCB.

- Zener diode 1N5222

This Zener diode is formed from glass with an orange body and a black stripe on one end. It is marked with a small “22”. The black stripe needs to align with the white stripe on the PCB silk screen.

- Zener diode 1N4733

This Zener diodes has a black body with a white stripe on one end and is larger than the other Zener diode. The white stripe on the body of the Zener diode needs to align with the white stripe on the PCB silk screen.

- Red 100 µF capacitors

The 100 µF capacitors have a white stripe which indicates the negative terminal. The negative terminal should align with the white bar (opposite the “+” bar) on the PCB silk screen.

- LM7805 voltage regulator

The LM7805 voltage regulator is in a small TO-92 package. The package is marked “L78L05”. Make sure its flat side matches the silk screen.

- Green LED

The green LED has a flat side which indicate the negative terminal. This flat side should align with the flat side of the PCB silk screen.

# General Guidance

- Reference the class soldering guide.
- You should take care with your soldering and align the resistors so their gold tolerance bands all face the bottom or right side of the board. This alignment will make it easier to compare your resistor locations with the pictures of the assembled board posted on the Canvas page.
- Solder in wire loops to the following pairs of terminals. Note I used trimmed resistor leads for this and they work great.
  - GND.1
  - VIN
- Do not solder in components for other subsystems.

# Testing the Power Subsystem

One you have completed assembly, perform the following checks. Please power the audio board on and off between checks.

Power subsystem

You should use a digital multimeter to make the following measurements.

- Power on causes the LED to illuminate
- 5V header is regulated to 5V +/- 0.1V
- 2.5V header is regulated to 2.5V +/- 0.1V

Intentionally apply reverse voltage to the inputs and verify that the current drawn by the power supply is essentially 0mA.

Audio Board: Power Supply

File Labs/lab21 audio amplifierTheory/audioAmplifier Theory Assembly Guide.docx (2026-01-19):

EENG 385 - Electronic Devices and Circuits

Audio Board: Amplifier Theory

Assembly Guide

Soldering Together the Amplifier Subsystem

You will be soldering the amplifier subsystem for the Audio board this week. The schematic is shown in Figure 1.

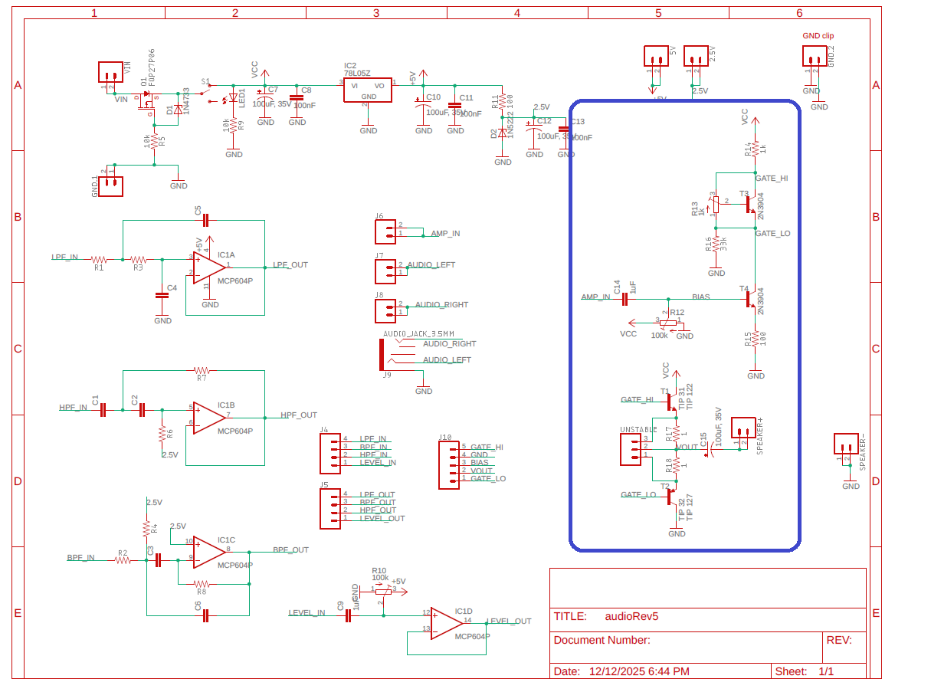
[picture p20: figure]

Figure 1: The schematic for the Audio board with the power subsystem circled in blue.

Like, your previous experiences, the parts in this schematic have a designator and a value. These designators are used to relate a part in the schematic with the layout. I converted the schematic in Figure 1 to the layout shown in Figure 2. As before, the physical position of the parts in the schematic and layout are unrelated, the schematic is an abstraction of the finished layout. The layout contains all the data used in the fabrication of the PCBs – the layout and the fabricated PCB are identical.


Figure 2: The layout of the Audio board with the power subsystem outlined in blue.

You should notice parts logically related in the schematic are physically proximal in the layout.

# Polarized Parts

Most of the parts to be soldered into the PCB can be installed in more than one way. Parts which must be installed in a correct orientation are called polarized. Polarized parts have some physical indication of their orientation, and the silk screen will have some markings to show you where this physical indicator should be aligned. Let’s walk through all the polarized parts that you will solder this week and how you will install them in the PCB.

- Red 100 µF capacitors

The 100 µF capacitors have a white stripe which indicates the negative terminal. The negative terminal should align with the white bar (opposite the “+” bar) on the PCB silk screen.

- TIP31 and TIP32 transistors

The TIP31 and TIP32 transistors are in TO-220 packages with metal tabs on the back. These metal tabs should face the edge of the board.

- 2N3904 transistor

The 2N3904 transistor is in a small TO-92 package - the package is marked “2N3904”. Make sure that its flat side matches the silk screen.

- Potentiometers

While potentiometers are not strictly polarized, you can install them either way and they will work properly, if you install them backwards, the silkscreen will not align to their function indicated on the silk screen. So, make sure to align the metal screw on the pot over the circle on the silk screen.

# General Guidance

- Reference the class soldering guide.
- You should take care with your soldering and align the resistors so their gold tolerance bands all face the bottom or right side of the board. This alignment will make it easier to compare your resistor locations with the pictures of the assembled board posted on the Canvas page.
- Solder in wire loops to the following pairs of terminals. Note I used trimmed resistor leads for this and they work great.
  - GND.2
- Solder in 2-pin headers into the following pairs of terminals
  - SPEAKER+
  - SPEAKER-
- Solder in a 2x3 header into the RIGHT, AMP_IN, LEFT headers
- Do NOT solder anything into the GATE_HI, GND, BIAS, VOUT GATE_LO headers
- Do not solder in components for the filter subsystems.

# Testing the Amplifier Subsystem

Until the pair of potentiometers are adjusted, your amplifier subsystem will not work properly. It would be best to have someone else check your component placement and orientations and check theirs. Then come to lab next week ready to learn how to adjust the potentiometers and get some sound from your amplifier.

Audio Board: Amplifier Theory

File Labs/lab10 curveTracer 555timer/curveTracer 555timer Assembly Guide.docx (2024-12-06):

EENG 385 - Electronic Devices and Circuits

BJT Curve Tracer: Intro to MultiSim and the 555 Timer

Assembly Guide

# Assemble: 555 Timer

This week, you will be soldering in the components associated with the POWER INPUT, 555 TIMER subsystems. These subsystems are names in Figure 9. It is important you do not solder in any of the other components in any of the other subsystems.

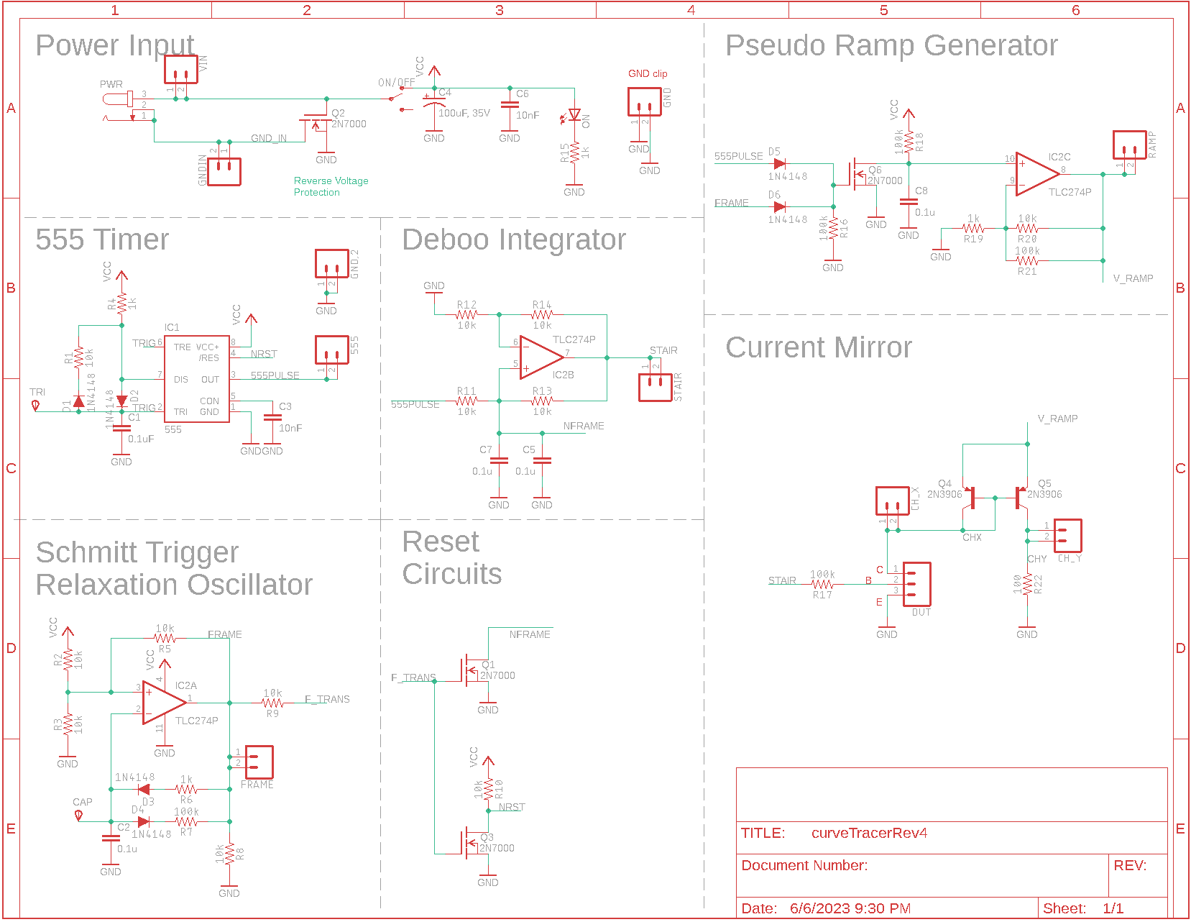
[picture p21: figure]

Figure 9: The schematic for the BJT curve tracer.

Most of the parts in this schematic have a designator and a value. The designator is a letter followed by a number. The designator letter tells you what type of part it is, “R” for resistor, “C” for capacitor, etc. The designator number tells you the index of that part in the entire collection of that part type.

The schematic in Figure 9 is the starting point for the layout shown in Figure 10. The physical position of the parts in the schematic and layout are unrelated. The schematic is an abstraction of the finished layout. The layout contains all the data used in the fabrication of the PCBs – the layout and the fabricated PCB are identical. Take a moment to look at the layout and compare it to the PCB for the curve tracer paying attention to the following bullet points.

- The green circles in Figure 10 are the layout are plated through holes in the PCB.
- The red lines in Figure 10 are traces (wires) on the top side of the PCB.
- The blue lines in Figure 10 are traces (wires) on the bottom side of the PCB.
- The grey lines and text in Figure 10 are white silk screen on the PCB.

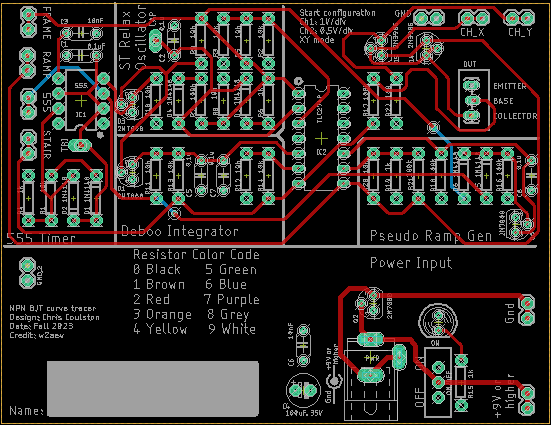
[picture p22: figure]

Figure 10: The layout of the BJT curve tracer.

The parts’ designators are important because they are the same in the schematic and the layout, providing you with a means to find a part. You should take a moment to notice parts which are logically related in the schematic are physically proximal in the layout.

Table 3: List of parts to be soldered into the PCB this week. Shaded cells are polarized components. Watch their orientation.

POWER INPUT | 555 TIMER
PWR JACK | R4/1kΩ
ON/OFF | R1/10kΩ
C4/100µF | D1/1N4148
C6/10nF | D2/1N4148
LED1 | C1/0.1uF
R15/1kΩ | C3/10nF
Q2/2N7000 | IC1/555

## Polarized Parts

Most of the parts you will solder into the PCB can be installed in more than one way. Parts which must be installed in a correct orientation are called polarized. Polarized parts have some physical indication of their orientation and the silk screen will have some marking to show you where this physical indicator should be aligned. Let’s walk through all the polarized parts and how you will install them in the PCB.

- 555 Timer

The chip has a small round indentation in the corner which indicates Pin 1. This indentation should align with the white circle on the PCB silk screen.

- Diodes

The diodes are orange with a black stripe on one end. The black strip needs to align with the white stripe on the PCB silk screen. Caution, the diodes do not have a consistent orientation – pay close attention when stuffing parts into the PCB.

- Red 100 µF capacitors

The 100 µF capacitors have a white stripe which indicates the negative terminal. The negative terminal should align with the white bar (opposite the “+” bar) on the PCB silk screen.

- Green LED

The green LED has a flat side which indicates the negative terminal. This flat side should align with the flat side of the PCB silk screen.

- 2N7000 MOSFET

The 2N7000 MOSFET is a 3-pin device with an asymmetrical package. You will have to bend the center lead of the MOSFET to make it fit. Make sure to align the flat side of the MOSFET with the flat side of the silk screen.

## Test Points

Test points are electrical connections to important points in the circuit and frequently are the target of test and measurement equipment. All the test points on the BJT curve tracer PCB are formed with pairs of pads. You will connect together each pair of test-point pads with an approximately 1 cm long piece of wire – you can use the cut off end of resistor lead for this. You will do this for all the test-point connections listed below – their names are labeled in white silk screen on the PCB.

1) CH_X
2) CH_Y
3) GND (adjacent to CH_X and CH_Y)
4) 555PULSE
5) STAIR
6) FRAME
7) GND (adjacent to 555PULSE)
8) +9V or higher
9) GND (adjacent to +9V)

An example of a test point that you will solder in this lab is shown in Figure 11. Note the TRI pad does NOT get a test point soldered into it.

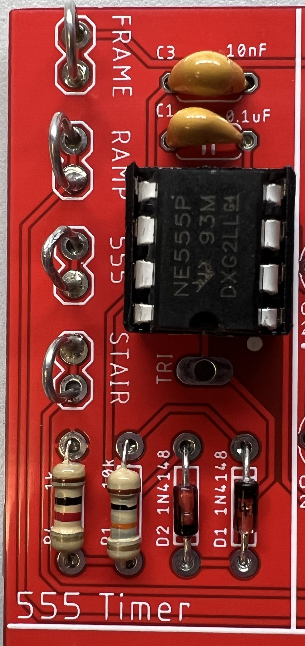
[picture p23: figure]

Figure 11: Wire loops soldered to the 555PULSE and FRAME test points. Do not solder in a wire loop to the TRI pin (just below the 555 timer).

# Assembly and Testing: 555 Timer

Work on being patient with the heat from the solder iron soaking into the PCB pad and the part leads. Use a small dab of liquid solder on the tip of the iron to facilitate heat transfer. When everything is nice and hot, the small dab of solder will wick onto the PCB pad and component lead. When this happens, start to melt a small length (less than the join will need) into the interface between the iron tip and the component and PCB pad. Remove the solder while leaving the soldering iron tip in place to make a quick appraisal: Can the joint can take a little more solder? If so, add another little dab of solder. When done, remove the solder first, then the iron. When you get the knack of it, this should take about 5 seconds. Work on improving your work from last week – take your time.

You should take care and align the resistors so their gold tolerance bands all face the bottom of the board. This positioning will make it easier to read their values and compare your work to pictures of the assembled board. This aspect will be part of the grading rubric. Look at the How To: Solder posted on Canvas for recommendation on how to solder through hole parts.

## Assemble POWER INPUT Subsystem

You should start your soldering with the POWER INPUT subsystem. The subsystem will include the following parts. Note, please check the component values of your capacitor and resistor with the component tester on top of the blue cabinet in the North West corner of Brown 304.

1) 100µF capacitor – POLARIZED!
2) Green LED – POLARIZED!
3) 2N7000 MOSFET – POLARIZED!
4) 10nF capacitor
5) Power jack
6) ON/OFF slide switch
7) 1kΩ resistor
8) +9V or higher test point
9) GND test point

After you solder in all the components, test and correct any problems before soldering any other components.

## Test POWER INPUT Subsystem

1) Check the resistance between the “+9V or higher” and GND test points with the ON/OFF switch in the OFF position. You should get an overload condition on the DMM – there is essentially infinite resistance with the switch in the OFF position.
2) Check the resistance between the “+9V or higher” and GND test points with the ON/OFF switch in the ON position. You should get a very high resistance due to the revere voltage protection provided by the 2N7000.
3) Power up the BJT curve tracer:
  - Put the ON/OFF switch in the OFF position,
  - Apply power to the board either through your AC/DC converter or using the lab power supply through the “+9V or Higher” and GND in the Power Input area. DO NOT USE ANY OF OTHER GND CONNECTIONS AS THE GROUND POWER INPUT. If you are using the lab power supply, set the voltage to 9V and the current to 100 mA.
  - Throw the ON/OFF switch to the ON position,
  - The green LED should illuminate.
    - If you are using an AC/DC converter to supply power, check the voltage at the “+9V or higher” and GND test points with a DMM. You should expect a volt or two higher than the AC/DC rated output voltage – they run high under low load conditions.
    - If you are using the lab power supply to provide power, the current should be less than 20 mA.

## Debugging POWER INPUT Subsystem

Doing anything drastically wrong when assembling the POWER INPUT subsystem is not common. I would expect most of the problems to be failures in your test procedure rather than failures of the board. If your BJT curve tracer board fails, one of the test steps in the previous section, I will provide some guidance on what may have happened and how you can correct it.

1) If you are getting low resistance with the ON/OFF switch in the OFF position:
  - Make sure the ON/OFF switch is in the OFF position
  - Check you do not have a solder bridge on the rear of your PCB
  - Make sure you are reading the DMM correctly. The reading when the ON/OFF switch in the OFF position should be the same as when you hold the probes apart in air.
2) If you are getting a different resistance with the ON/OFF switch in the ON position:
  - Make sure the ON/OFF switch is in the ON position
  - Make sure you are reading the DMM correctly. The reading when the ON/OFF switch in the ON position should be the same as when you hold the probes across a spare 1 kΩ resistor.
  - Check the orientation of the green LED. The part may be installed backwards.
3) If the green LED does not illuminate when power is applied to the ON/OFF switch when it is in the ON position:
  - Test you are applying power. Put a DMM in voltage mode and check the +9V and GND test points.
  - Check the orientation of the green LED. The part may be installed backwards.
  - Check the solder joints on the 1 kΩ resistor and the green LED. When you attempt to wiggle either of these two components, they should not move at all.

## Assemble 555 TIMER Subsystem

You should start your soldering with the POWER INPUT subsystem. After you solder in all the components, you should test and correct any problems. This soldering task will include the following parts. Note, please check the component values of your capacitor and resistor with the component tester on top of the blue cabinet in the North West corner of Brown 304.

1) 8-pin socket for 555 Timer – Install so that circular indent aligns with silk screen.
2) 555 Timer IC – POLARIZED!
3) 1N4148 diodes – POLARIZED!
4) 10 nF and 0.1uF capacitors
5) 1 kΩ and 10 kΩ resistors
6) 555PULSE test point

## Test 555 TIMER Subsystem

1) Power up the BJT curve tracer.
  - Put the ON/OFF switch in the OFF position.
  - Apply power to the board either through your AC/DC converter or using the lab power supply. If you are using the lab power supply, set the voltage to 9V and the current to 100 mA.
  - Throw the ON/OFF switch to the ON position.
  - The green LED should illuminate.
    - If you are using an AC/DC converter to supply power, check the voltage at the “+9V or higher” and “Gnd” test points with a DMM. You should expect a voltage higher than the AC/DC rated output voltage. Converters run high under low load conditions.
    - If you are using the lab power supply to provide power, the current should be less than 50 mA.
2) Power up an oscilloscope, attach a probe to Channel 1 and configure it as follows.

Ch 1 probe | 555PULSE testpoint
Ch 1 ground clip | BJT ground loop
Horizontal (scale) | 200 µs
Ch 1 (scale) | 1V or 2V (whatever fits better)
Ch 2 probe | TRI pin of 555 Timer
Ch 2 (scale) | 2V
Trigger mode | Auto
Trigger source | Ch 1
Trigger slope | ↑
Trigger level | 4.5V

3) Set the GND reference of Ch 1 and Ch 2 to the lowest visible reticule. The waveforms will overlap the same as they did in the MultiSim simulation. The TRI pin of the 555 Timer is available by remove the end of the oscilloscope probe and putting the tip into the yellow circled pad in Figure 12. Note that this pad is labeled “TRI”.

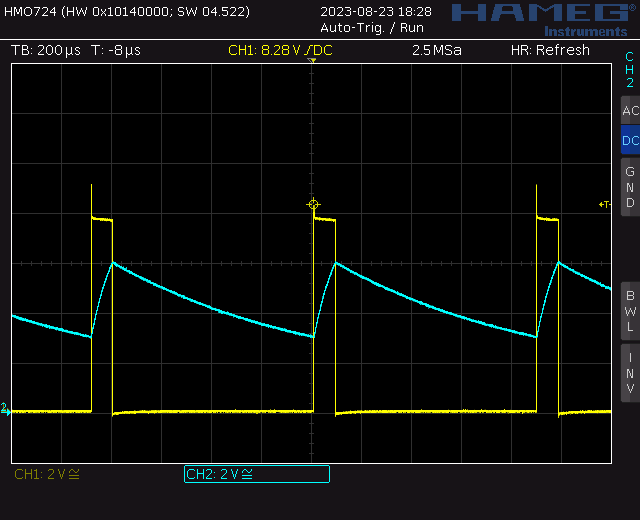
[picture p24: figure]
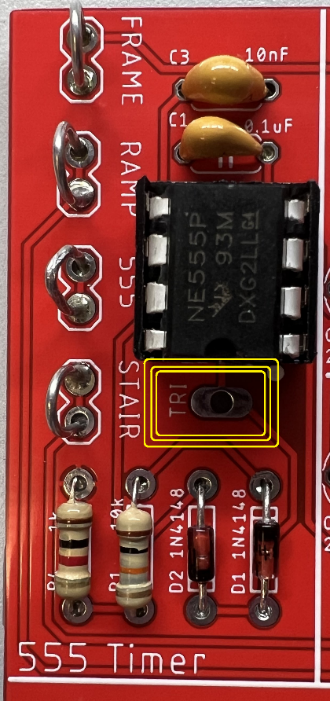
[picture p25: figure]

Figure 12: (Let) The TRI pin of the 555 Timer is available at the circled pad. Note, this oscilloscope trace was captured on a Rhode&Schwarz HMO724.

4) Take a screen shot of the two waveforms and include in your lab report. Screen shot the oscilloscope traces on USB. Cell phone pictures will lose points. [Save] → Save → Format → 24-bit Bit... (*.bmp) [Save] → Save → Press to Save

## Debugging 555 TIMER Subsystem

Compare to the POWER INPUT subsystem, there are many more ways to foul up the 555 TIMER subsystem. If your BJT curve tracer board fails one of the test steps in the previous section, I will provide some guidance on what may have happened and how to correct it.

1) If the green LED is no longer illuminating when you apply power to the BJT curve tracer:
  - Verify you are applying power to the BJT curve tracer by probing the +9V and Gnd test points with a DMM in voltage mode and with the ON/OFF switch in the ON position.
  - Verify the ON/OFF switch is in the ON position.
  - Check the orientation of the 555 Timer IC.
2) If the 555 Timer is not generating a proper waveform:
  - Make sure the 555 TIMER parts are inserted in the correct location.
  - Check the orientation of all the 555 TIMER parts.

BJT Curve Tracer: Intro to MultiSim and the 555 Timer

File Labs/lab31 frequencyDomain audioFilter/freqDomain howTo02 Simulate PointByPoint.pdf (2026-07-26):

## How To: Simulation Bode Plot – Point by Point

Let’s construct the low pass filter (LPF) in Figure 1 using LTspice.

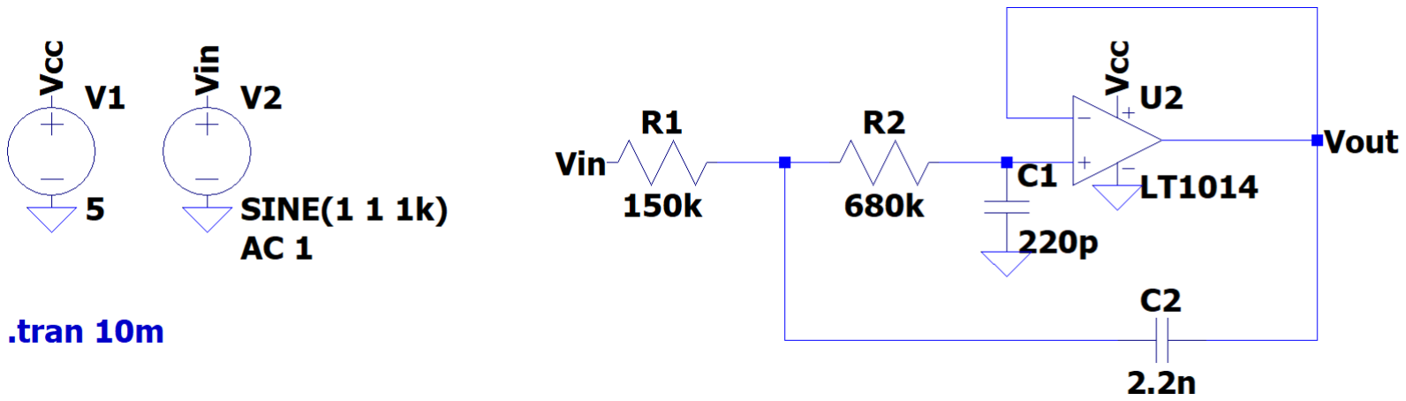
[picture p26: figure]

Figure 1: The low-pass filter on the Audio board is built around an op amp powered by 5V and gnd.

The 5V DC supply, V1, for the op amp is an important detail copied over from the real Audio board filter. Voltage source V2 provides a 1kHz sinusoid input to the LPF. When you place a voltage source, go to the Advanced options, select the SINE radio button and make the following :

- | DC offset[V] | 1
- Amplitude[V] 1
- | Freq[Hz] | 1k

The op amp in Figure 1 (and on your Audio board) is powered from 5V and 0V. For the LPF and the BPF this will cause problems if your input signal has no DC bias. “No DC bias” means that the input sine wave is centered at 0V - the audio input to your Audio board has no DC bias. In our simulation, the DC bias is provided by the 1V DC offset of V2. On your Audio board, the DC bias is provided by the level shifter.

With this out of the way, generate the waveforms in Figure 1. After probing Vin and Vout, your waveforms should be identical to Figure 2.

EENG 385 - Electronic Devices and Circuits Frequency Domain: Active Filters How To: Use Simulator to Build a Bode Plot Using Point-by-Point method

Frequency Domain: Theory and Practice of Filter Design

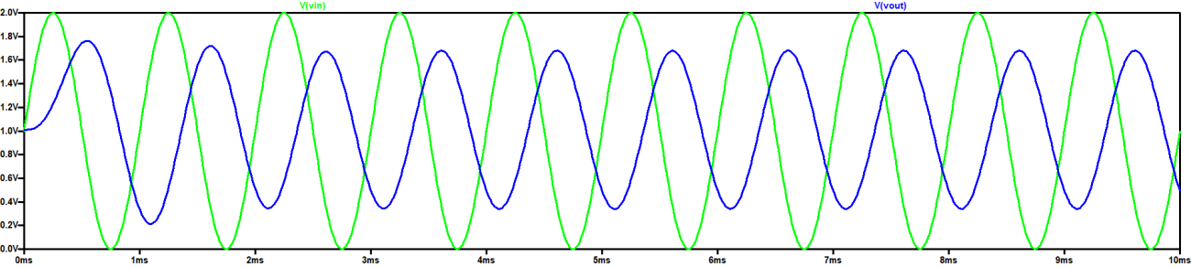
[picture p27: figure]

Figure 2: A 1,000Hz input waveform (in green) and the output(blue) from the low-pass filter.

From this graph, you should be able to see that the output waveform has a lower amplitude than the input. This change in amplitude, from input to output, is called attenuation. Mathematically, attenuation is the ratio of the output over the input. You will form this ration to normalize the output amplitude in terms of the input amplitude. Since we will be measuring very large ranges of attenuation, you will measure attenuation in units of decibels by using the following equation.

attenuation in decibels = 20 ∗ log(

Vout
Vin

⁄ )

Let’s measure the attention, in decibels, of the waveforms in Figure 2.

- By observations, Vin is 2.00V peak-to-peak
- Using the cursors on the Vout, it is 1.36V peak-to-peak

Thus at 1,000 Hz, the low-pass filter has 20*log(1.36/2.00) = -3.3dB of attenuation.

In addition to the change in the amplitude, the output waveform is delayed with respect to the input waveform. This shift in time is called phase delay. Phase delay is measured in degrees that the output waveform occurs with respect to the input waveform. Let’s measure the phase delay of the output in Figure 2. Start by choosing any peak of the input; I’ll choose the peak at 2.25ms. Now look for the peak in the output that immediately follows the input. This occurs at 2.6ms. To find the phase angle, divide the time different between these two peaks by the period of the waveform; (2.25ms – 2.6ms)/1ms = -0.35. Finally, multiply this value by 360° to get the phase delay; -0.35*360° = -126°.

So, at 1,000Hz the low pass filter in Figure 1 has -3.3dB of attenuation and -126° of phase shift. A Bode plot is a pair of graphs describing the attenuation and phase shift of a circuit as a function of frequency. You can build a Bode plot by repeating the calculations in the previous paragraph multiple times. So, let’s give it a try.

Start by downloading and opening the filterWorkSheet posted on the Canvas page. Go to the LPFsim tab and fill in value for Vout/Vin for 1000Hz row and enter the ratio of the output over the input; 0.75 in cell C9. The corresponding decibel entry will auto populate in the Attenuation column. Next enter the time delay between the peaks of the input and output waveforms in units of milliseconds in the Delta (ms) column; -0.35 in cell E9. The corresponding Phase entry will auto-populate in the Phase column.

Now change the frequency of the input waveform in LTspice to every frequency value in column B that is not already filled in. Some technical notes:

Frequency Domain: Theory and Practice of Filter Design

- When you get to higher frequencies, the amplitude of the output waveform will be so small that it becomes hard to measure. When this happens, zoom in with thin wide zoom rectangles.
- With the mouse pointing at an axis, you can translate along the axis using the cursor keys.
- If the output waveform will not stay centered at 1.0V, determine the amplitude over a single wavelength. Do you best.
- To measure the phase, I left one x-axis cursor at a peak of the input and then zoomed in on the vertical axis until I could move the other x-axis cursor to an output peak.

I’d like to take a moment and draw your attention to the frequencies you used as the input frequencies and listed in column B of the spreadsheet. Note that these frequencies follow a pattern of 1.0, 2.2, 4.7 before repeating at the next power of 10. As an electrical engineer you would say that we have 3 different frequencies per decade. These 3 frequencies are separated by a multiplicative factor of √10 ³ = 2.15 ≈ 2.2. When you plot numbers whose x values are separated by a multiplicative factor of 2.15 on a logarithmic horizontal axis the points appear equally separated along the axis. This is a result of the fact that log(2.15n) = n ∗ log(2.15). So in short, using a geometric factor to increase frequencies ensures the points are space equally along a logarithmic axis. Neat huh?

You can usually copy graphs from Excel and paste them into Word. At worst you can use the windows snipping tool to make a copy of your Bode plot. Try to make the graph reasonably large so that the graders can read the units in the horizontal and vertical axes.

Now you are ready to complete the plots asked for in the assignment – good luck!

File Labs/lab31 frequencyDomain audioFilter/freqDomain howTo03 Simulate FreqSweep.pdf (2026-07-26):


1

## How To: Simulation Bode Plot – Frequency Sweep

In the previous How To, you built a Bode plot for the circuit shown in Figure 1.

Figure 1: The low-pass filter on the Audio board is built around an op amp powered by 5V and gnd.

Now that you have gone through the painful process of building a Bode plot by hand, you will be delighted to know there is a far easier method to do this, have LTspice do it for you; the AC Analysis tool. The AC Analysis function runs a series of simulations, each:

- Will have an incrementally higher frequency for the AC source, V2 in Figure 1. You set the range of frequencies for the AC source,
- Will record the amplitude of each probe in the circuit in decibels with respect to the amplitude of the AC source,
- Will record the phase of each probe in the circuit in degrees with the phase of the AC source being 0°,

The waveform window will display the recorded data as magnitude and phase versus frequency. The frequency axis is logarithmic, forming a Bode plot for each probe in the circuit.

Let’s try this out for our low-pass filter in Figure 1. Start by selecting the Configuration Analysis

icon in the top toolbar. In the pop-up, select the AC Analysis tab. We will use the same settings as you used in the point-by-point method to generate the Bode plots in Excel.

- | Type of sweep: | Decade
- Number of points per decade: 20
- | Start frequency | 1Hz
- | Stop frequency | 47kHz

EENG 385 - Electronic Devices and Circuits Frequency Domain: Active Filters How To: Use Simulator to Build a Bode Plot Using Frequency Sweep Method

Frequency Domain: Theory and Practice of Filter Design

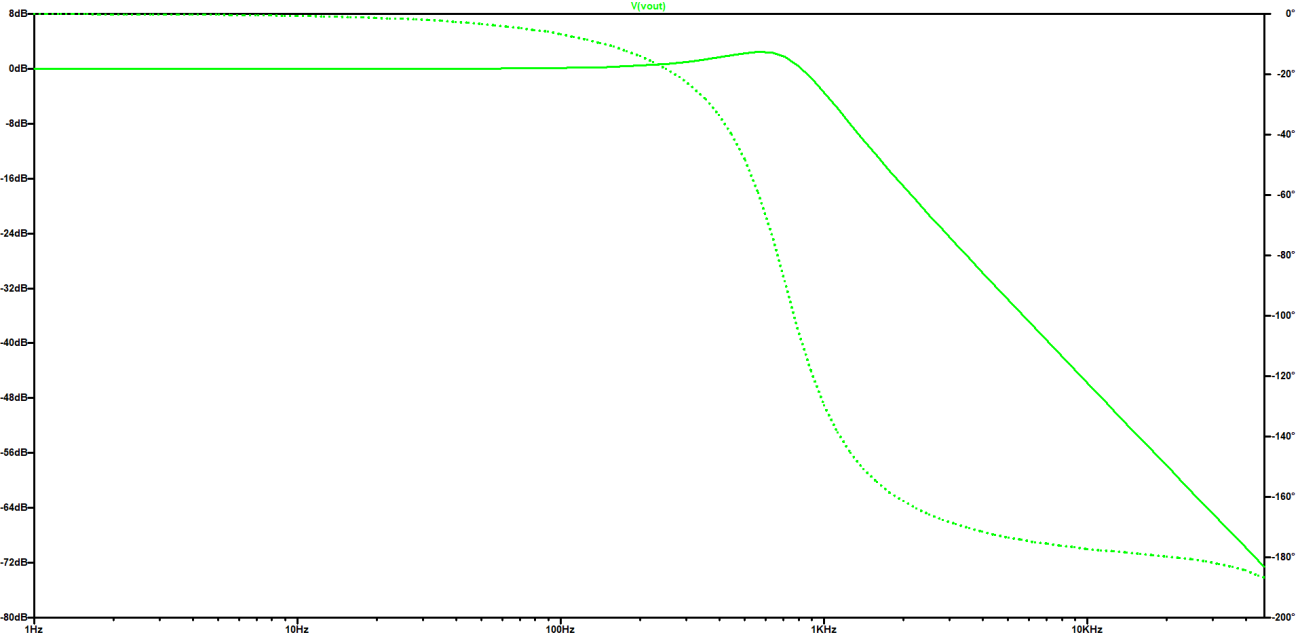
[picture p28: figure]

2

Click OK and your cursor is replaced with the text “.ac dec 6 1 47k”. Place this text near your AC source then run the simulation by clicking the green arrow in the top toolbar. The output shown in Figure 2 has the attenuation scale on the left axis and the phase scale on the right axis.

Figure 2: The grapher output after running a frequency sweep on the circuit in .

You are now ready to generate all the Bode plots needed for this lab, good luck!

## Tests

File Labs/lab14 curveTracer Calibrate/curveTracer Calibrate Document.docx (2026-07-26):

EENG 385 - Electronic Devices and Circuits

BJT Curve Tracer: Calibration

Lab Document

# Outcome and Objectives

The outcome of this lab is to complete the assembly of the BJT curve tracer and display the characteristic curve of a BJT on an oscilloscope display. Through this process you will achieve the following learning objectives:

- Analyze and design a circuit consisting of several building blocks.
- Assemble a circuit on a PCB using the equipment in the laboratory.
- Use laboratory test and measurement equipment to analyze electronic circuits.

# Generating Characteristic Curves

Within the lab, you will complete the construction and calibration of the BJT curve tracer, a circuit using an oscilloscope in X/Y mode to display the family of curves shown in Figure 1 (right) for a BJT acting as the device under test (DUT) Figure 1 (left).

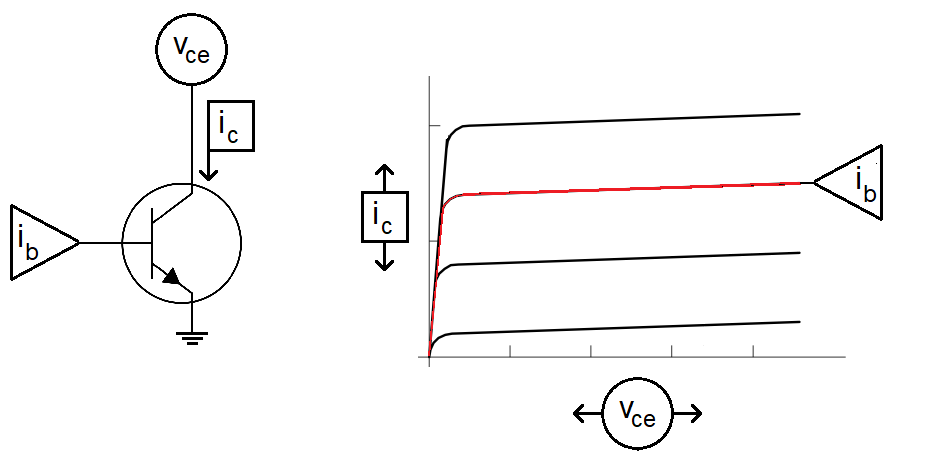
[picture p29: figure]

Figure 1: (Left) The signals needed to generate the characteristic family of curves for a BJT under test include Ib, the base current, Ic the collector current, and Vce the collector emitter voltage. (Right) The family of Ic vs. Vce curves as drawn on the oscilloscope.

To generate the red curve in Figure 1 (right), we need to complete the following 3 plotting tasks:

1. Set the base current to the red value in Figure 1 (right).
2. Then, sweep the collector emitter voltage from 0V to 5V.
3. Then, while doing the sweep, measure the collector current.

Fortunately, we have built most of the circuits needed to accomplish the task in the previous labs. These circuits interface with the DUT and the current mirror shown in Figure 2 to generate the signals shown in Figure 1.

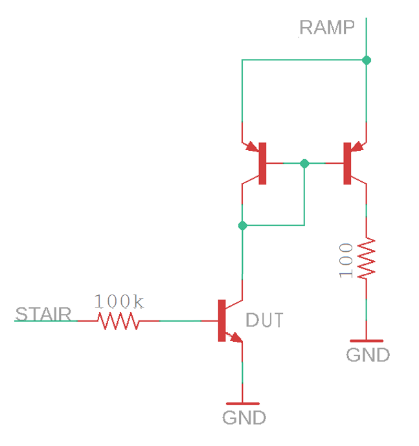
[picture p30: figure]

Figure 2: The output stage of the BJT curve tracer uses a current mirror to measure the collector current.

The list of plotting tasks is reframed in terms of the circuit shown in Figure 2 as:

1) The STAIR voltage is fed into the base of the DUT through a 100 kΩ resistor, setting the base current.
2) The collector emitter voltage of the DUT sweeps from 0V to 5V using the output of the pseudo ramp generator.
3) The collector current of the DUT is indirectly measured, through the current mirror, as the voltage across a 100 Ω resistor.

Now, we need a way to plot the collector emitter voltage against the collector current. This need is where the X/Y mode of the oscilloscope comes into its own.

# Oscilloscope: X/Y Mode

You have mainly used oscilloscopes in time-base mode, meaning the voltage on Channel 1 is plotted vs. time. You can imagine the voltage on Channel 1 controls the height of the beam as the beam is being swept across the display. In X/Y mode, the oscilloscope uses the voltage on Channel 1 to control the horizontal position (x-axis) of the beam and, at the same time, uses the voltage on Channel 2 to control the vertical position (y-axis) of the beam.

At first, this interaction sounds really weird and counter intuitive. However, you can do some pretty useful things with an oscilloscope in X/Y mode, like drawing the family of curves for a BJT. To explore this idea further, let’s work the following example. Use the voltages on Channel 1 and 2 in Figure 3 to determine what is displayed with the oscilloscope is X/Y mode. In this example, the following conditions are set.

- Ch 1 is configured to provide x-axis data.
- Ch 2 is configured to provide y-axis data.
- The vertical axis for Ch1 and Ch2 is 1 Volt per division.
- The center horizontal line is set to 0V.

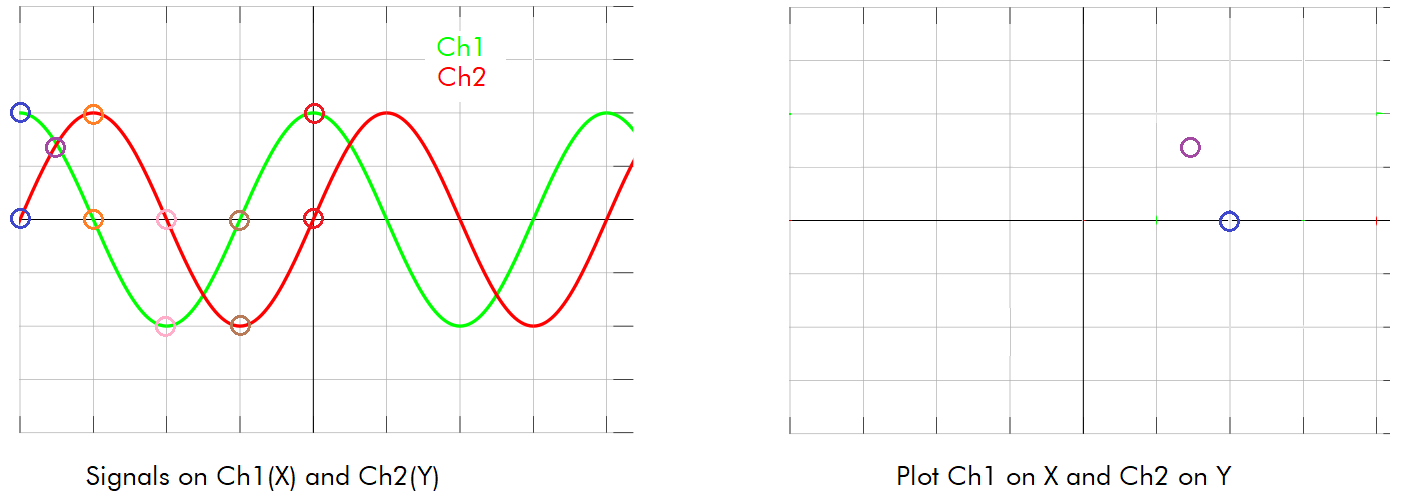
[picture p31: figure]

Figure 3: A pair of signals on Channel 1 and Channel 2. Plot these 2 signals in XY mode.

At the left edge of the screen, the values of Ch 1 and Ch 2 are circled in blue, with Ch 1=2V and Ch 2=0V. So in the right half of Figure 3, a blue circle is placed at (x,y) = (2V, 0V). Note, the X/Y plot has the same scale as its respective channel.

Complete Table 1 by finding the voltages for Channel 1 and Channel 2 at the indicated times. Then, place these points on the X/Y plot, connect the dots, and determine what the user would see. The key to determining the scales of the X- and Y-axis in Figure 4 is the circuit which drives the X and Y signals, shown in Figure 5.

Table 1: The X,Y values of the curve in Figure 3.

Time | Ch 1 (X) | Ch 2 (Y)
Blue
Purple | | 1.4
Orange
Pink
Brown | 0
Red

# Oscilloscope: Axis Scale for BJT Curve Tracer

We need a way to convert the picture shown on the oscilloscope into numerical data informing us of the operation of the BJT. You will quantify the picture on the oscilloscope using the grid displayed on the oscilloscope screen and by the scale settings you establish by turning the Ch 1 and Ch 2 vertical scale knobs. Some notation is in order before proceeding.

- Let VSCALE_X be the volts per division set with the Ch 1 Vertical scale knob. This number is shown after the yellow “1” in the upper left corner of the oscilloscope screen.
- Let VSCALE_Y be the volts per division set with the Ch 2 Vertical scale knob. This number is shown after the green “2” in the upper left corner of the oscilloscope screen.
- Call the distance between the grid lines shown on the oscilloscope face “divisions”.

For example, in Figure 4, VSCALE_X = 500 mV/div and VSCALE_Y = 200 mV/div. The X1 and X2 cursors are about 8.4 divisions apart.

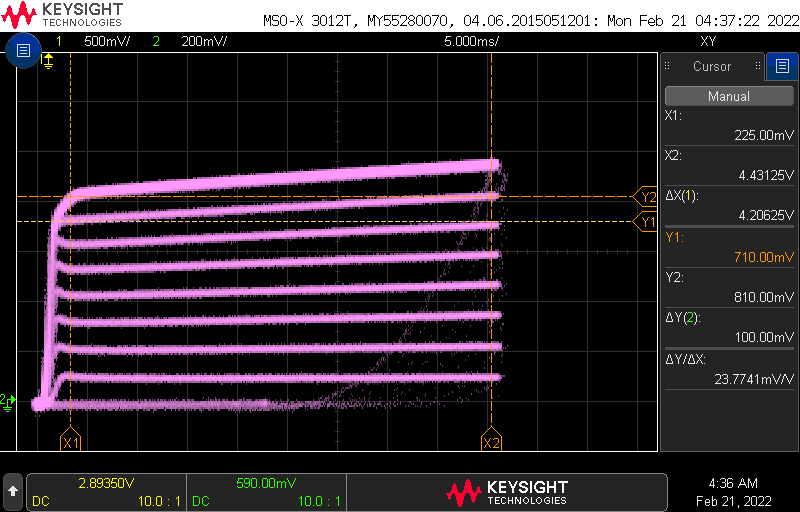
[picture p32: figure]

Figure 4: The oscilloscope display showing the family of curves.

The key to finding an equation allowing us to convert the picture on the oscilloscope screen to numerical values is the circuits which drive the X and Y signals shown in Figure 5.

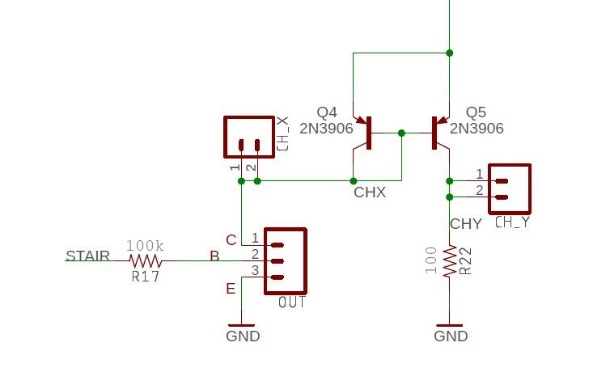
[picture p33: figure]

Figure 5: The circuit generating the 2-channels for the X-Y mode.

Let’s start by examining the Horizontal Axis scale.

## The Horizontal Axis Scale – Collector Emitter Voltage

You will connect Channel 1 of the oscilloscope to CH_X in Figure 5 and as a result probe to the collector of the DUT. Since the emitter of the DUT is at ground, CH_X is measuring Vce of the DUT. Thus, we have Equation 1:

| V_(ce) = V_(CH_X) | 1

Now let’s focus on the collector current measured on Channel 2 of the oscilloscope.

## The Vertical Axis Scale – Collector Current

You will connect Channel 2 of the oscilloscope to CH_Y in Figure 5. Note that Q4 and Q5 are arranged as a current mirror, meaning the collector current out of Q4 is equal to the collector current out of Q5. Since the current out of Q4 is the collector current, ic, of the DUT then the current output of Q5 is also equal to ic. Thus, the collector current is equal to the current flowing through the 100Ω resistor. The voltage at the CH_Y probe in Figure 5 is found using Ohm’s law and given by Equation 2.

| v_(CH_Y) =i_c *100Ω | 2

Solving Equation 2 for the collector current is easy enough. The equality in Equation 4 is formed by replacing 100Ω with its Ohm’s law equivalent 10mA/V.

| i_c = (V_(CH_Y))/(100Ω)=(10mA)/(volt)*V_(CH_Y) | 3

## Test Your Understanding

Let’s try to use the two ideas just presented to determine Vce and ic of the points marked in Figure 6. Do this by first converting the position of the square into voltage. You need to know two things in order to perform this conversion.

- The x-axis is scaled at 1V/division and the y-axis is scaled at 0.2V/division.
- The 0V,0V is located at the red square (pointed at by the small yellow and blue arrows)

Now, the orange square is located 1 division to the right of the red square, hence it has an x-axis voltage of 1V; thus, by Equation 1, Vce = 1V. The orange square is 4 divisions above the red square, hence, it has a y-axis voltage of 4 divisions * 0.2V/division = 0.8V; hence, by Equation 4, ic = 0.8V * 10mA/volt = 8mA.

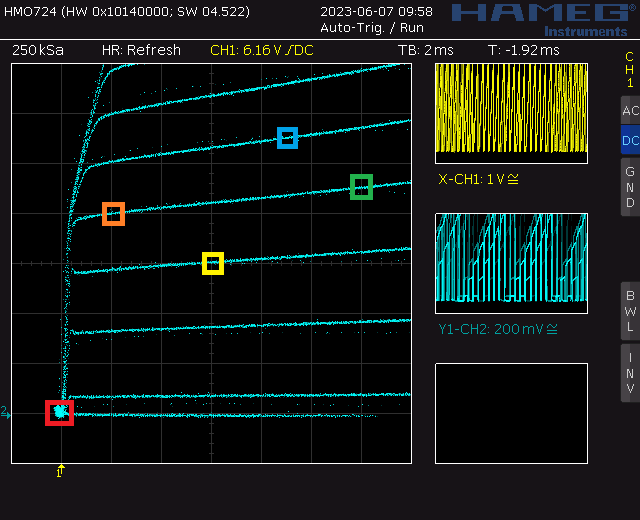
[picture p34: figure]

Figure 6: A family of curves with colored squares marking points to determine Vce and ic.

Table 2: Complete the table using the information in Figure 6.

Square | VCHX | Vce | VCHY | ic
Red | 0 | 0 | 0 V | 0 mA
Orange | 1V | 1V | 0.8V | 8mA
Yellow
Green
Blue

## Each Curve – Base Current

The circuit in Figure 5 keeps the DUT transistor in the active region. Thus, the BE junction of the DUT has about a 0.7V drop. Since the emitter of the DUT is grounded, the base of the DUT is at 0.7V. Let’s call the voltage at the STAIR signal VSTAIR. You can use a combination of KVL and Ohm’s law to compute the voltage drop from VSTAIR to ground as:

| V_(STAIR) - i_b *100kΩ-0.7V=0 | 4

Solving Equation 4 for ib yields Equation 5.

| i_b =(V_(STAIR) -0.7)/(100kΩ) | 5

Computing the base current for each value of VSTAIR requires you to carefully measure the voltage of each step. Note, you can perform this measurement before soldering in the new components associated with this lab. To get these values, start by powering up your BJT curve tracer board with 9V from the lab power supplies. Next, power up an oscilloscope, attach a probe to Channel 1 and configure the oscilloscope as follows:

Ch1 probe | STAIR test point
Ch1 ground clip | GND test point
Horizontal (scale) | 1ms
Ch1 (scale) | 1V or 2V (whatever fits better)
Trigger mode | Auto
Trigger source | Ch1
Trigger slope | ↓
Trigger level | 4.5V

You should get something that looks like the curve in Figure 7.

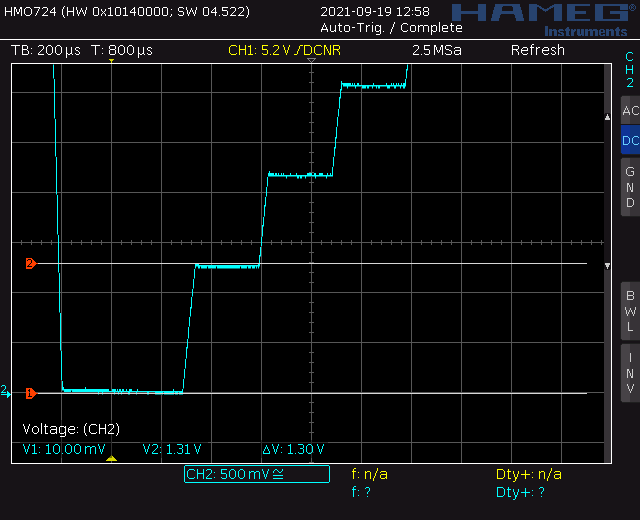
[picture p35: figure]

Figure 7: Measuring the voltage of the first VSTAIR value using cursors to be about 1.3V.

Now, measure the voltage of each step and record the values in the VSTAIR column of Table 3. Note, Trace 0 never leaves 0V. Trace 1 is the first trace above Trace 0 and should be around 1.3v. Your values will be different from those given in Table 3.

Table 3: The base current for each step of the staircase function. Yes the VSTAIR voltage are different from those shown in Figure 7.

Trace | VSTAIR (V) | ib (µA)
8 | ---- | ----
7 | ---- | ----
6 | 7.6 | 15uA
5 | 6.4 | 12uA
4 | 5.1 | 9.4uA
3 | 3.9 | 6.8uA
2 | 2.6 | 4.0uA
1 | 1.4 | 1.5uA
0 | 0 | 0

Now, use the voltages in the VSTAIR column of Table 3 to compute the base current, ib, using Equation 5. You will need the information in Table 3 every time you run the BJT curve tracer with a DUT. Let’s explore how to use this information to calculate the gain and Early Voltage of the DUT.

# Completing the BJT Performance Card for a BJT

By completing the BJT performance card, you will be able to determine two important parameters of the BJT under test, the DC gain and the Early voltage. To determine these parameters, download and open the bjtPerformanceCard.docx Word document posted on Canvas. The document should look similar to Figure 8. Use the information from Table 3 to fill in the ib column in the table circled in red in Figure 8. While you are at it, fill in your name in the Name field and the identity of the BJT in the Device ID field. Since your BJT curve tracer is unique to you and the information in Table 3 will not change, you will save a personal copy of the bjtPerformanceCard document with this information typed in permanently.

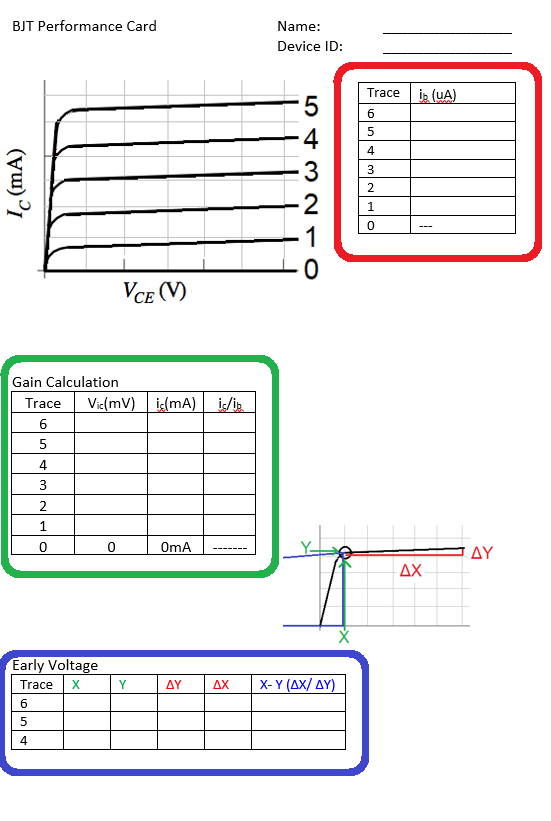
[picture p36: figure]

Figure 8: The BJT Performance card you will complete for every DUT. Text will be colored red, orange, or green when it describes how to fill in the BJT Performance Card table circled in that color.

By filling in this information, you have taken the first step in computing the Gain Calculation table outlined in green. Let us see what other information is need to collect and compute in order to complete the Gain Calculation table.

Start by powering the BJT Curve Tracer with 9V from a lab power supply. Next, you will need to setup your oscilloscope as shown in the following table. Note, you may need to adjust this configuration depending on the DUT.

Horizontal (scale) | 5 ms
Ch1 probe | CH_X
Ch1 (scale) | 0.5V/div
Ch 1(position) | Lowest visible reticule
Ch2 probe | CH_Y
Ch2 (scale) | 0.2V/div
Ch 2(position) | Lowest visible reticule
Trigger mode | Auto

Finally connect the test BJT to the DUT socket.

You should see a rather chaotic set of waveforms as those shown in Figure 9 with activity on both channels. If either channel has no signal, make sure the DUT is firmly inserted into the test fixture or check if the DUT is inserted backwards. (Some BJTs have the collector and emitter terminals swapped.) Adjust the ground reference of both channels to the lowest visible reticule.

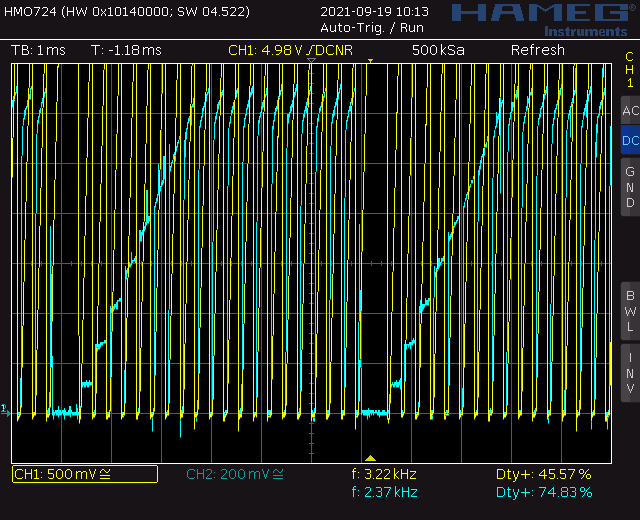
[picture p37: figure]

Figure 9: The oscilloscope output with a DUT in normal mode.

Next, you will need to put the oscilloscope into X/Y mode. Find the Horiz button and then use the softkey menu to select X/Y.

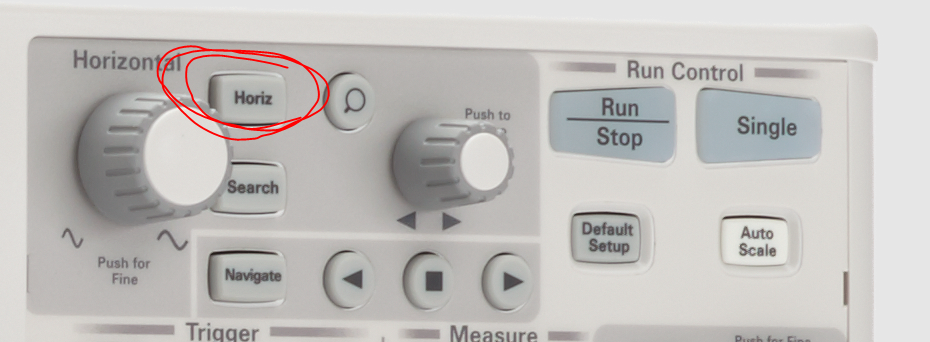
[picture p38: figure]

Figure 10: Display showing the placement of the Horiz button.

You may start out with an image that look like Figure 11.


Figure 11: X-Y mode when first enabled. You need to adjust the voltage scale and offset to make the curves recognizable.

Use the Channel 1 and Channel 2 scale knobs on the oscilloscope to make the curves larger like that shown in Figure 12


Figure 12: Use the Channel 1/2 scale knobs to change the width/height of the curves respectively.

Next use the Channel 1 and Channel 2 offset knobs to move the curves to the lower left corner of the display, while you are doing this, you can use the scale knobs to produce an image like that shown in Figure 13.


Figure 13: Use the Channel 1/2 offset knobs to move the curves horz/vert respectively.

You should adjust the horizontal scale to enhance the family of curves. You can experiment with the intensity (using the small button below the adjust knob) to tune your picture like that shown in Figure 14 (left). You can also try Acquire -> High Resolution Model to greatly sharpen the image at the expense of added noise on the display Figure 14 (right). Use whatever you prefer.


Figure 14: Use the intensity (left) or High Resolution Mode to sharpen the curves.

Congratulations, you have your BJT curve tracer working! Let’s figure out how to get numerical information from the plot to complete the Gain Calculation portion to the BJT Performance Card.

## Gain Calculation

You will use the cursor function of the oscilloscope to measure the collector current and use this to determine the current gain.

You will need to measure the collector current for each curve at Vce = 1v. Start by enabling the cursor function by pressing the Cursor hard key. Pressing the Cursor soft key brings up a menu of the four cursors you can adjust. You can change the active cursor using the adjust knob (has a green illuminate circular arrow next to it). You can adjust the position of the active cursors using the Measure knob. Start by adjusting the X1 and Y1 cursors to 0v (look at the lower right area of the display to see the voltage of each cursor). Next adjust the X2 cursor to 1v; this makes the X2 cursor lie at Vce = 1V. Finally adjust the Y2 cursor to the intersection of the X2 cursor and the curve you whose collector current you want to measure.


Figure 15: Using the cursors to measure the collector current of the 3rd curve.

In Figure 15, the Y2 cursor is at 400mV. You will record this value in the Vic column of Table 3 in row 3 because this is the third curve in the family. You should keep the Y2 cursor selected and adjust its position using the Measurement knob. This will enable you to determine all the collector current voltages for the different curves. Note, feel free to change the vertical scale or offset to better position the curves for measurement.

When any of the following text is color-coded red or green, it refers to one of the circled areas in Figure 8. The data in this section will be a combination of the information contained in Figure 15 and the base currents found in Table 3. Your values will be different than those shown here.

1. Now, you need to fill in the green-circled area to determine the collector current for each of the curves. You will do this by recording the voltage of each curve as it passes Vce = 1V and put them into the Vic column. Use the cursor procedure discussed at the beginning of the section.

Table 4: The Gain Calculation table filled in using the information from Figure 15 and Table 3. These gains are unreasonably high and have too much variation.

Trace | Vic(mV) | ic(mA) | ib(uA) | ic / ib
6 | 1.04 | 10 | 15uA | 666
5 | 0.9 | 9.0 | 12uA | 750
4 | 0.72 | 7.2 | 9.4uA | 766
3 | 0.56 | 5.6 | 6.8uA | 824
2 | 0.4 | 4 | 4.0uA | 1000
1 | 0.2 | 2 | 1.5uA | 1333
0 | 0 | 0 | 0 | 0

2. Fill in the collector current column, ic, by multiplying the entries in the Vic column by the channel 2 conversion factor of 10mA/V Round your answers to 2 significant figures.
3. Copy the base currents from Table 3 into the ib column.
4. Finally, fill in the ic / ib column, the gain of the DUT, by dividing each collector current by its associated base current. Make sure you account for the change in units; mA for the collector current and uA for the base current.

Congratulations, you have calculated the gain of your DUT! You will get different gain values for different base currents. Asking for a single value of gain across a variety of base currents is pointless because the gain of a BJT has a weak dependence on the collector current. You can look in a BJT datasheet and verify this for yourself. So, we have to be satisfied with the values in our Gain Calculation table even if the values change with base/collector current.

## Early Voltage

The Early voltage is the projection of the almost-horizontal portion of the characteristic curve and where it will intersect the horizontal axis. The black curve in Figure 16 is one of the characteristic curves for the BJT displayed on the oscilloscope. The hypotenuse of the blue triangle is the projection of the sloped horizontal portion of the characteristic curve. The horizontal axis is the collector emitter voltage and consequently has the units of volts. The point where the hypotenuse of the blue triangle intersects the horizontal axis is the Early voltage. Early voltages are always negative.


Figure 16: Calculating the Early voltage requires working with the red and blue similar triangles.

The red and blue triangles in Figure 16 have the same interior angles and as a consequence are similar. This means that the ratio of their bases and heights are equal. In other words.

(∆x)/(∆y)=X/Y which we can solve for X and get X=Y(∆x)/(∆y) The Early voltage is equal to X shifted right by Xo. This gives us the final equation for the Early voltage in terms of the data gathered from the oscilloscope using the cursor function.

Early voltage=X_o -Y(∆x)/(∆y)

You will measure the Early voltage using cursor function of the oscilloscope as follows. Like before, enable the cursor function by pressing the Cursor hard key. Set the X1 cursor to 1V, the X2 cursor to 5V (or the biggest integer voltage that will fit on your screen). Set the Y1 cursor to the intersection of the X1 cursor and the curve whose Early voltage you want to measure. Finally set the Y2 cursor to the intersection of the X2 cursor and the curve whose Early voltage you want to measure.


Figure 17: Measuring the Early voltage of the 6th curve using the cursors.

The right side of the screen provides all the information that you will need to fill in the information in Table 4. To take the remaining measurements, leave the X1 and X2 cursors, and adjust the Y1 and Y2 cursors to measure the slope of the remaining curves. You may want to change the vertical offset to better see the curves.

We will examine Trace #6 in Figure 17 to explain how you will compute the Early voltage for your DUT. In the active region, Trace #6 is a straight line sloping upwards. Use the cursor function and align the X1 and Y1 cursors at the left end of the active region, where the curve is flat. Next align the X2 and Y2 cursors on the right end of the active region. You can use the X1 and X2 markers at the bottom of the screen and the Y1, Y2 markers on the right side of the screen to interpret the values shown on the right-side menu of the oscilloscope display.

Table 5: The Ealy Voltage table partially filled in using the data from Figure 17.

Trace | X1 | Y1 | ΔY | ΔX | X-Y (ΔX/ ΔY)
8 | 1 | 1.22 | 0.123 | 4
7 | 1 | 1.08 | | 4 | -40
6 | 1 | | 0.083 | 4 | -43

The Early Voltage is given by the value in the X-Y (ΔX/ ΔY) column. The data for the 7th and 8th curves is provided so that you have a sense of the expected variation in this measurement.

# Turn In:

Make a record of your response to numbered items below and turn them in to Canvas using the instructions posted there. While you can work together to answer the questions in this lab document, this is an individual assignment. Thus, everyone is expected to turn in their own document.

Hint, use Ctrl+click to follow links. This also works for all the Figures and Tables in these labs.

Oscilloscope in X/Y Mode

Completed Figure 3.

Completed Table 1.

Axis Scale for BJT Curve Tracer

Completed Table 2.

Completed Table 3 using data from your BJT curve tracer

Completing the BJT Performance Card for a BJT

Completed Table 4.

Completed Table 5.

Complete a BJT Performance Card for the 2N3904 BJT in a TO-92 package.

  - Determine the pinout for the Base, Emitter, and Collector from an online datasheet.

Complete a BJT Performance Card for the 2N2222 BJT in a TO-92 package.

  - Determine the pinout for the Base, Emitter, and Collector from an online datasheet.

Complete a BJT Performance Card for the BD139 in a TO-126 package.

  - Determine the pinout for the Base, Emitter, and Collector from an online datasheet.

BJT Curve Tracer: Calibration

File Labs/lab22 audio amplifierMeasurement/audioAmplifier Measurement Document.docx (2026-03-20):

EENG 385 - Electronic Devices and Circuits

Audio Board: Amplifier Measurements

Lab Handout

# Outcome and Objectives

The outcome of this lab is the proper adjustment of the Vbe multiplier and DC offset of the audio amplifier to produce high-fidelity audio output. Through this process you will achieve the following learning objectives:

- Perform a DC and AC analysis of a circuit containing BJT.
- Analyze and design a circuit containing one or more BJTs.
- Use laboratory test and measurement equipment to analyze electronic circuits.

# Audio Amplifier Calibration

The heart of the Audio Amplifier is shown in the schematic in Figure 1. Today you will calibrate the bias voltage and Vbe voltage and then use your audio amplifier. To do this, you will need to refer to your previous week’s lab calculations. So, before you start, access this document and keep it handy.


Figure 1: The core of the audio amplifier consists of a voltage gain stage followed by a current gain stage.

## 20 Turn Potentiometer

Last week you soldered in a pair of 20-turn potentiometers, a 1kΩ and 100kΩ like that shown in the left side of Figure 2. Look closely at the notation imprinted on the surface of the potentiometer in Figure 2 and you will see the letters “CW” printed next to the number 3. This means that as you turn the brass adjustment screw in a ClockWise (CW) direction the center tap (terminal 2) moves closer to the left pin (terminal 3). This is accomplished using a worm drive mechanism; the brass adjustment screw engages a gear attached to the center tap. The geared center tap moves around the carbon track connecting terminals 1 and 3. The worm drive acts like a gear reduction; this means that you need to rotate the brass adjustment screw 20 times to move the center tap from terminal 1 to terminal 3 (or vice versa). Note that the rotating the brass adjustment screw Counterclockwise (CCW) moves the center tap towards the right pin (terminal 1).


Figure 2: The internal structure of a 20-turn potentiometer.

## Audio Signal and the 3.5mm Audio Cable

This should be no surprise to you, but when you put on a pair of headphones to listen to music, your left and right ears hear slightly different audio, producing stereo sound. The Audio Board accepts stereo inputs from the 3-pole TRS cable shown in Figure 3. TRS stands for Tip, Ring, Sleeve, which refers to 3 metallic sections of the connector. You will connect an audio source to one end of the 3-pole TRS cable and the other end into the mating audio jack on the Audio Board, at right in Figure 3. The left/right audio channel from the TRS cable will be available on the pair of headers labeled LEFT/RIGHT on the Audio board. Notice that the two LEFT headers are connected together with a wire (red line in Figure 3), so they carry identical signals. Same with the RIGHT headers.

You will apply a signal to the AMPIN header in Figure 3 to send an audio signal to the amplifier. The header pins in Figure 3 are placed 0.1” apart so you can use a 2-pin jumper to connect the LEFT or RIGHT audio channel to AMPIN. Unless you are dealing with a mono audio source (an audio source with a single channel), it does not matter if you send the LEFT or RIGHT audio channel to the AMPIN pin.


Figure 3: left, a 3-pole TRS cable audio cable. Center, the Audio board stereo input connector and associated header pins. Right, a 2 pin jumper used to connect the LEFT or RIGHT audio channel to AMPIN.

# Configure the Audio Board

Before you start work on today’s lab you need to perform an initial setup of your audio board. After soldering your components from last week your board will look something like that shown in Figure 4 with the exception of the components in the lower left corner, which you should NOT have installed.


Figure 4: These are three items that need immediate attention before you start the lab. You should NOT have any components soldered into the lower left area of the board labeled LPF, HPF, BPF, LEVEL.

Note, if you soldered in your potentiometers upside-down, your brass screws will be towards the top of the board. Do not resolder your board, just reverse the CW, CCW directions in the instructions below.

- Vbe Multiplier POT (left one)
  - Turn the brass adjustment screw clock-wise (CW) at least 20 turns. Until it clicks
- Vbias POT (right one)
  - Turn the brass adjustment screw counter-clock-wise (CCW) for at least 20 turns. Until it clicks.
  - Then turn the brass adjustment screw clock-wise (CW) for exactly 4 turns.
- Install a jumper on the lower two header pins on the right side.
- Configure Lab power supply channel 1
  - Vmax= 16V
  - Imax = 0.2A
  - Connect power supply to your board, turn ON/OFF switch OFF.
- Login to the lab computers
  - Launch a web browser
  - Load youtube.com
  - Run the video “1000 Hz Sine Wave The Ultimate 10 Hour Test Tone | 1kHz”
  - Experiment so you know how to adjust the volume, then pause the video.
- Grab a 3.5mm audio cable
- Grab a 2” speaker

# Calibrate With an Audio Signal

Let’s apply an audio to the amplifier and fine tune the bias voltage and Vbe multiplier in preparation to apply an audio signal. To do this, first configure your oscilloscope as follows:

Horizontal (scale) | 500us
Ch1 probe | GATE_LO header
Ch1 (scale) | 2V/div
Ch1 (coupling) | DC
Ch2 probe | GATE_HIGH header
Ch2 (scale) | 2V/div
Ch2 (coupling) | DC
Trigger source | 1
Trigger slope | ↑
Trigger level | 8V

Make sure to align the channel 1 and 2 ground references to the bottom edge of the oscilloscope display.

## Tune Bias Voltage

Adjusting the bias voltage changes the DC operating point of the output transistors T1 and T2 in Figure 1 which in turn determines VOUT. You can think of the operating point as the average value of the VOUT signal, its middle value. To get this right, perform the following.

1) Power on your audio board so that the green LED lights up.
2) Start the youtube audio producing an unplesant high pitch tone from your lab computer.
3) Next connect the PC to the audio board using the 3.5mm audio jack and the green 3.5mm jack on the back of the PC. The sound will stop from the PC when you have this correct.

Now adjust the Vbias potentiometer so that VOUT is centered at 8V. Figure 5 shows how this will look on the oscilloscope.


Figure 5: (left) The default waveforms from the GATE_HI and GATE_LO pins when you follow the steps in the CONFIGURE AUDIO BOARD section. (right) After some adjustment you should be able to get channel 1 centered at 8V.

## Tune Vbe Multiplier

It’s important to get the Vbe multiplier tuned because this is the one items that will cause the output transistors to overheat. In other words, if your output transistors are overheating it’s almost certainly a result of your Vbe multiplier being mis-adjusted. It is MUCH easier to set the BIAS voltage with a speaker attached.

Adjusting the Vbe multiplier changes when the T1 and T2, in Figure 1, conduct. When you set the voltage across the Vbe multiplier too high, both T1 and T2 will conduct at the same time. This will cause a short circuit between the Vcc and GND rails causing very high power disipation in T1 and T2. When you set the voltage across the Vbe multiplier is set too low, there will be times when neither T1 and T2 forward conduct. This will cause a flat spot in VOUT and a distorted audio output.

Both of these unwanted situations are a mistiming in turning one of the output transistors on, and turning the other transistor on too. This is called cross-over distortion because the output signal is crossing over from one of the transistors to the other. You need to adjust the Vbe multiplier so that the sinusoidal output has no cross-over distortion, so that the output waveform has no distortions in the middle. Figure 6 shows how to adjust the VBE potentiometer to eliminate cross over distortion.

Your oscilloscope should display the image at left in Figure 6. Now start to turn the Vbe POT in the CCW direction. After a bunch of turns (10 or more), you should start to see the waveforms separate. When you get them to about 2V (center in Figure 6), start monitoring the power supply as you continue to turn the Vbe POT in the CCW direction. At some point the current drawn from the power supply will rapidly jump – this marks the point where both T1 and T2 are turned on at the same time and you are shorting the power supply through T1 and T2. This is not a good thing, so back off the Vbe POT by turning it CW until the current drops back to what it was before (around 10mA to 20mA). If you are not paying attention to the power supply, you will notice that the channel 1 and channel 2 waveforms start to lose voltage when the Vbe POT is turned too far CCW as shown at right in Figure 6.


Figure 6: (left) The default waveforms from the GATE_HI and GATE_LO pins after centering channel 1 at 8V in the previous step. (middle) After some CCW adjustment on the Vbe POT, I separated the two waveforms by about 2.4V – perfect. (right) when the Vbe POT is turned too far CCW, you are shorting the power supply across the T1 and T2 Darlington pairs – bad.

## Re-Tune Bias Voltage

In the previous step you may have moved the waveforms away from the 8V center value. Adjust the Vbias POT to recenter the pair of waveforms so that their average value is 8V. You are now ready to do some further testing with your audio amplifier.

# Amplifier Measurements

Compute the voltage gain from the signal source to the Vout by forming the ratio of Vout amplitude over Vin amplitude. Note that this is the same quantity as the Vef/Vs ratio you computed in last week’s lab. In order to do this reconfigure your oscilloscope as follows:

Horizontal (scale) | 1ms
Ch1 probe | AMP_IN jumper
Ch1 (scale) | 0.2V/div
Ch1 (coupling) | DC
Ch2 probe | Vout header
Ch2 (scale) | 2V/div
Ch2 (coupling) | DC
Trigger source | 1
Trigger slope | ↑
Trigger level | 8V

Make sure to align the channel 1 and 2 ground references to the bottom edge of the oscilloscope display.

Some notes about this measurement:

- Center the input on the lower half of the oscilloscope display and center the output in the upper half.
- Use the Acquire function to smooth out the waveforms.
- Consider using the measurement tool to measure the amplitude.
- A 180° phase change from input to output represents a negative gain.

Screen shot the oscilloscope and use the values on the oscilloscope to compute the gain. The data shown in Figure 7 has a gain of 1140mV/129mV = -8.8. This is close to the gain of -10 that you should have gotten in last week’s lab for the unloaded Vef/Vs ratio.


Figure 7: Oscilloscope capture of an unloaded common emitter input and output - no speaker attached.

Now connect a speaker to and screen shot the oscilloscope. Use the values on the oscilloscope to compute the gain of the loaded amplifier. The data shown in Figure 8 has a gain of 516mV/129mV = -4. This is close to the gain of -4.4 that you should have gotten in last week’s lab for the unloaded Vef/Vs ratio.


Figure 8: Oscilloscope capture of a loaded common emitter input and output – 8 Ω speaker attached.

As a final test let’s use the oscilloscope’s built in frequency response subsystem to generate a Bode plot of the unloaded amplifier. To perform this test:

- Disconnect the 3.5mm audio cable and stop the youtube video.
- Connect a T-connector to function generator output of the oscilloscope. The function generator output of the oscilloscope is just above the power button.
- Connect BNC to BNC cable from T-connector to Channel 1 input
- Connect function generator cable from T-connector to AMPIN pin with the red alligator clip and GND loop to the black alligator clip. You will need a small jumper wire to connect the red alligator clip to the AMPin header pin. The left AMPin pin is electrically connected to the right AMPin pin so it doesn’t matter which you connect to.
- Connect Channel 2 to the VOUT header on amplifier board.
- Press the Analysis button (just above the Ch2 vertical scale knob)
- Press the Features softkey and select FRA
- Make sure the setup tab (gear icon) is selected
  - Frequency Mode Sweep
  - Frequency (Start, Stop) 10Hz 1MHz
  - Points per decade 10
  - Source (Input, Output) 1 2
  - WaveGen 200mVpp 50Ω
- Press Run Analysis. The screen displays the input and output waveform as data is bring collected.
- The graph tab should auto select and display the Bode Plot for the audio amplifier.

# Apply an Audio Source

Reconnect your 3.5mm audio cable between an audio source and the audio board. Put some tunes on and listen to the output. Enjoy, you’ve earned it.

# Turn In

Make a record of your response to numbered items below and turn them in a single copy as your team’s solution on Canvas using the instructions posted there. Include the names of both team members at the top of your solutions. Use complete English sentences to introduce what each of the following listed items (below) is and how it was derived.

Amplifier Measurements

Screen shot of input and output with no-load

Calculation of no-load gain

Screen shot of input and output with 8Ω speaker

Calculation of 8Ω gain.

Bode plot for amplifier

Apply an Audio Source

Demo working amplifier by playing a song

Audio Board: Amplifier Measurements

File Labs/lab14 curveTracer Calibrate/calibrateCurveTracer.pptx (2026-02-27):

## EENG 385 BJT Curve Tracer Calibration

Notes: Usually the <title of the lab> is what will be called the “System” through the rest of this document

## Lab Objectives

- Objective: Finish assembly of BJT Curve Tracer and use it to measure the gain and Early voltage of three BJTs.

## Theory

- Device Under Test = DUT
- Draw family of characteristic curves on oscilloscope
- Provide vce and ib as inputs then measure ic as the output


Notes: Replace <System> with the name of the

## Theory

- Imagine oscilloscope drawing an image using a beam
  - Oscilloscopes used CRTs
- X-position of beam
  - Controlled by voltage on Ch1
- Y-position of beam
  - Controlled by voltage on Ch2
- Can create complex images
  - IC vs. VCE family of curves

The Cathode-Ray Tube
Oscilloscope Art - YouTube

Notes: Replace <System> with the name of the

## Analyze

- Ramp - 0.7V is applied to collector of DUT
- Current mirror converts ic into voltage across 100Ω
- VSTAIR is converted to base current through 100kΩ
  - You will measure the voltage of each step convert to base current
  - You can do this before soldering in components

Step | VSTAIR(V) | ib (uA)
6 | 7.6 | 15
5 | 6.4 | 12
4 | 5.1 | 9.4
3 | 3.9 | 6.8
2 | 2.6 | 4.0
1 | 1.4 | 1.5
0 | 0V | 0


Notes: Replace <System> with the name of the

## Assemble

- Two 2N3906 PNP in 385 parts bin
- One 2N7000 NMOS in 385 parts bin
- Misc. resistors and 3-pin DUT socket in parts bin
- Use resistor leads for GND, CH_X and CH_Y loops


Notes: Replace <System> with the name of the

## Matching transistors

- Current mirror
  - Circled in red
  - Works perfectly when beta are same
- Choose
  - Same font = same lot
  - Use DCA75 Pro measure Beta

Picture 1 of 6

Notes: Replace <System> with the name of the

## Test

- Different BJTs will have different pinouts
- Will not harm DUT BJT if you put it in backwards
- Check datasheet for pinout
- Use jumper wires as needed


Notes: Replace <System> with the name of the

## Test

- Base current from Table 3
- Measure Vic at vce = 1V
- Use cursors for Early voltage


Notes: Replace <System> with the name of the

## Turn In

- This is an individual assignment – turn in your performance cards
- You can work in teams of two during this lab
- Fill out 3 BJT Performance Cards for:
  - 2N2222 (in 385 parts bin)
  - 2N3904 (in 385 parts bin)
  - BD139 (in 385 parts bin)
  - !!!RETURN WHEN DONE!!!
- Save BJT card as PDF
- Due before start of class next week
- Every student uses their own board
- Everyone brings their board to class

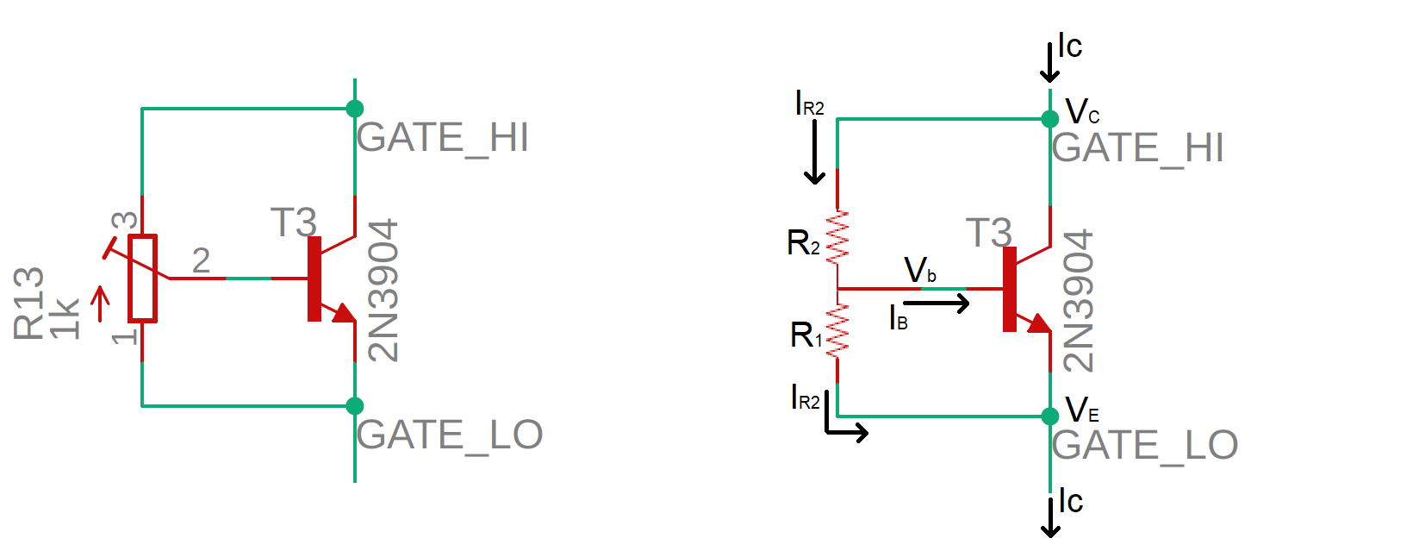
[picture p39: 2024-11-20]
Labs/lab22 audio amplifierMeasurement/img/VbeMultiplier.bmp

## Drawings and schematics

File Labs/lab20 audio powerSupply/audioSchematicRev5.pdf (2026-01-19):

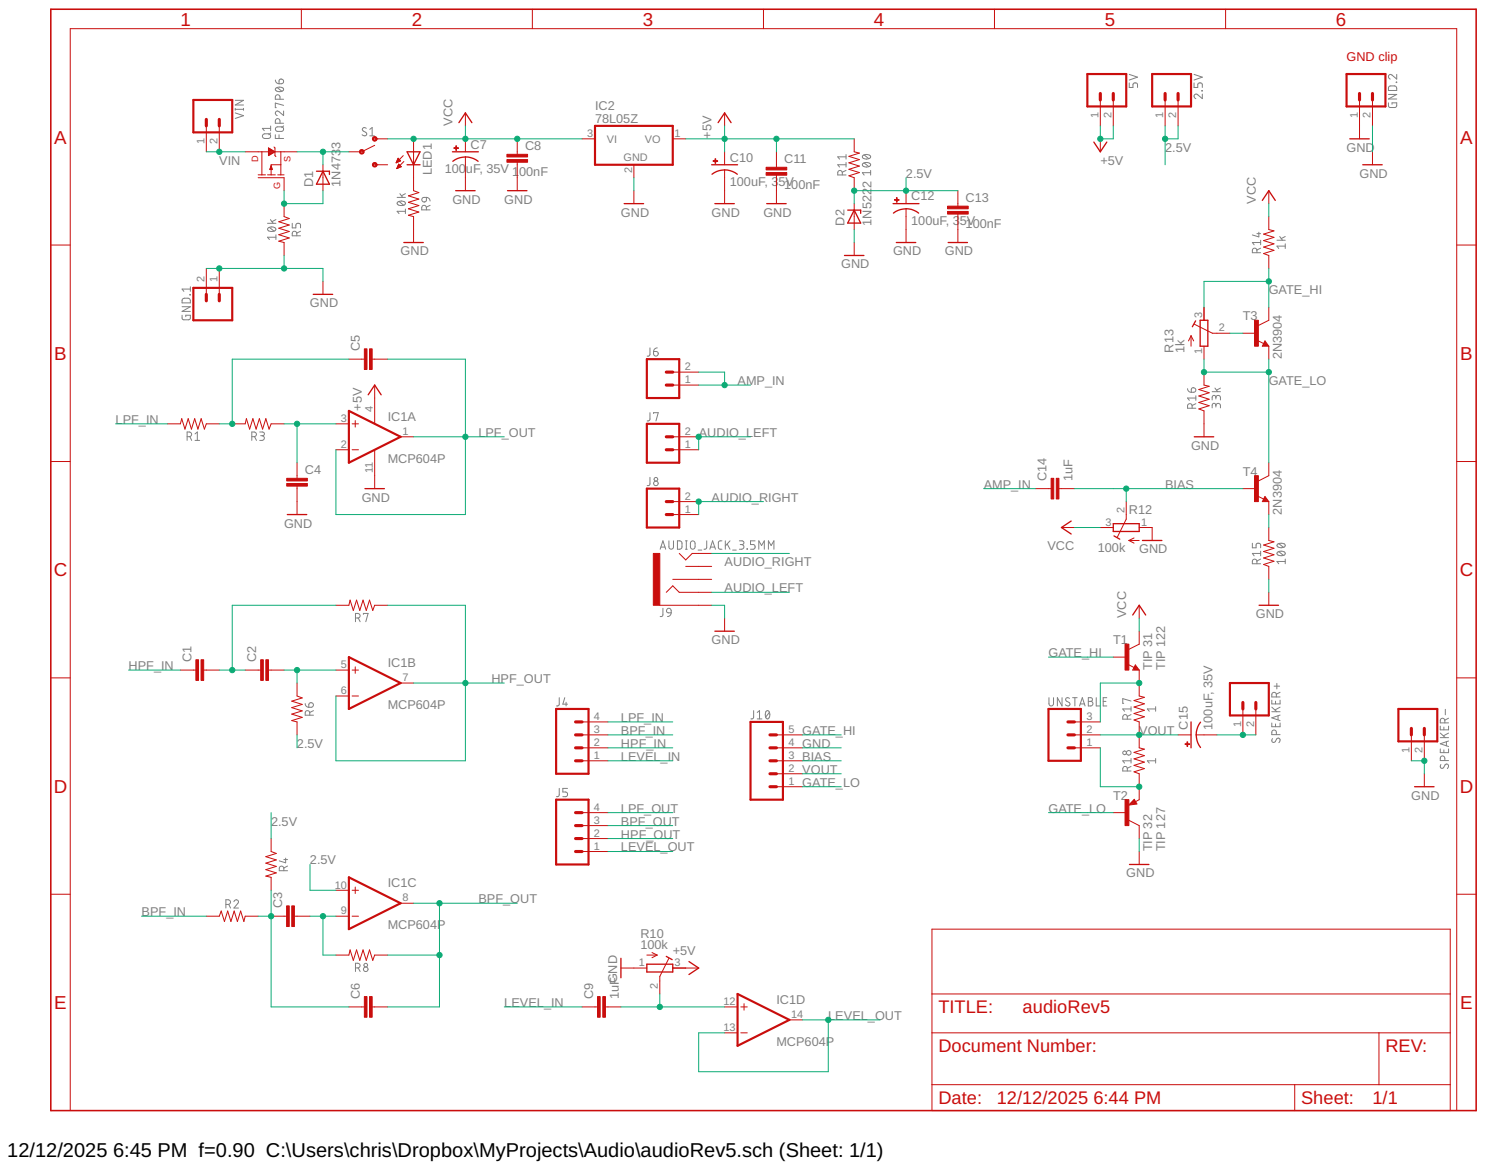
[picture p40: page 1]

Document Number: | REV:

Date: 12/12/2025 6:44 PM | Sheet: 1/1

12/12/2025 6:45 PM f=0.90 C:\Users\chris\Dropbox\MyProjects\Audio\audioRev5.sch (Sheet: 1/1)

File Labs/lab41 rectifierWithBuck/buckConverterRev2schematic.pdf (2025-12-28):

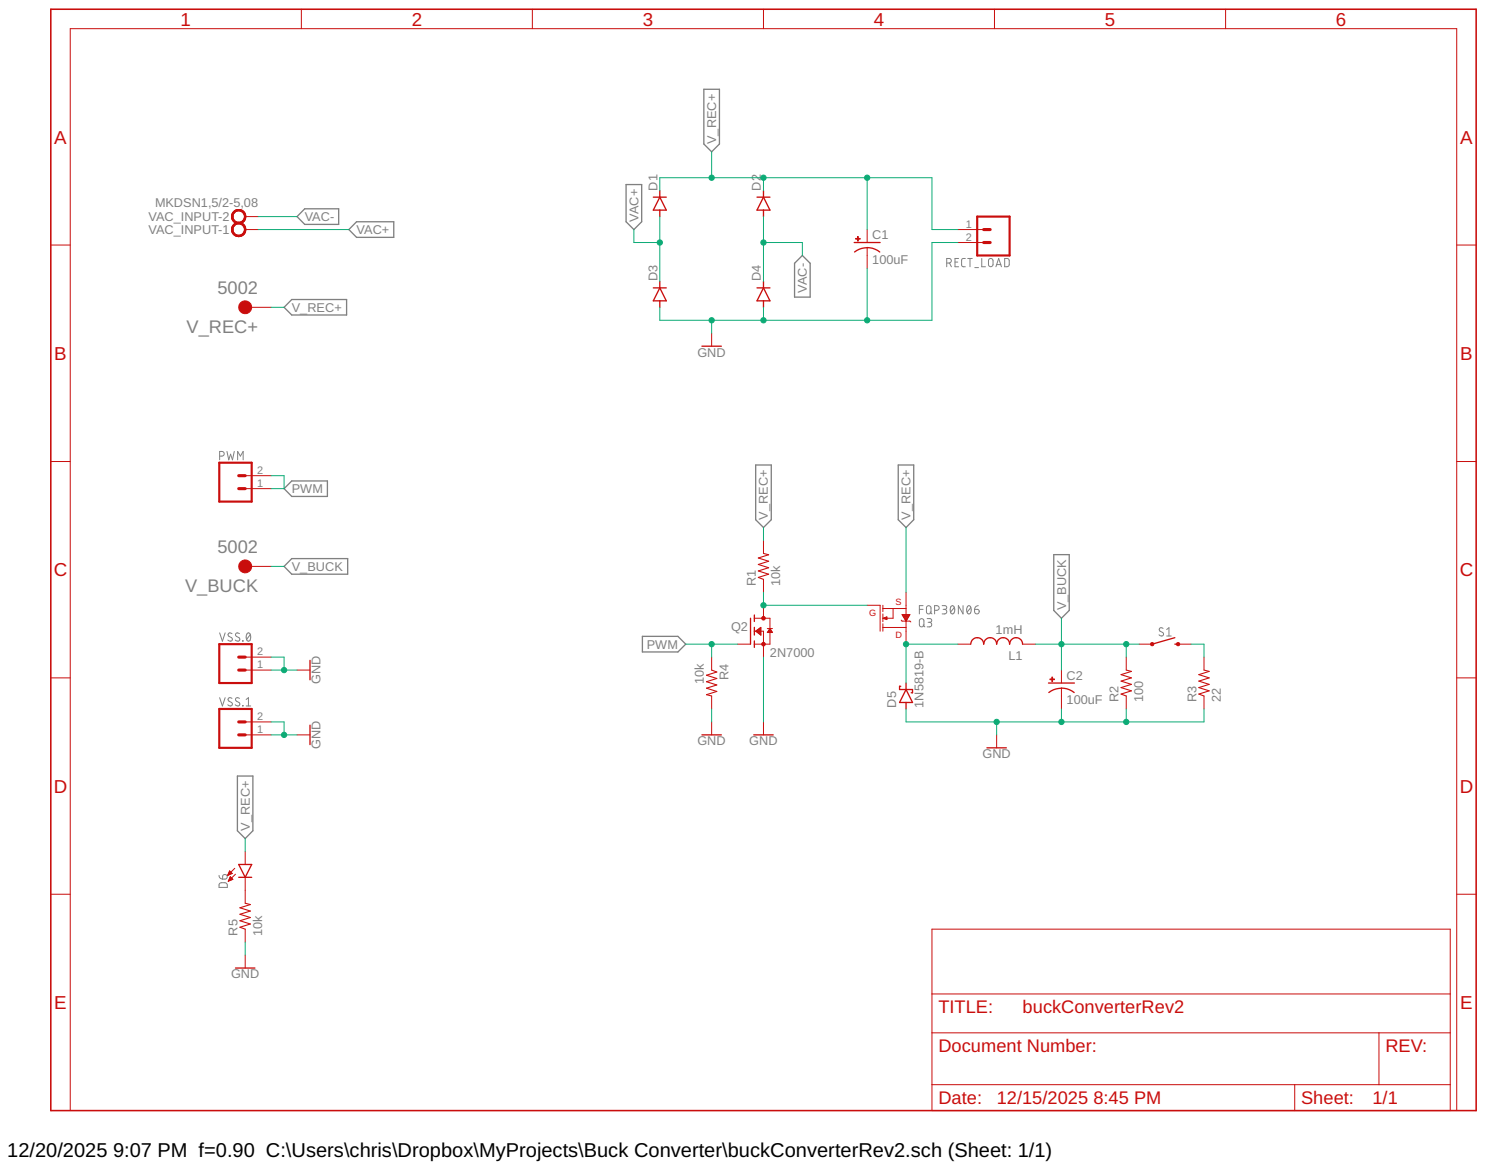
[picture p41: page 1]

Document Number: | REV:

Date: 12/15/2025 8:45 PM | Sheet: 1/1

12/20/2025 9:07 PM f=0.90 C:\Users\chris\Dropbox\MyProjects\Buck Converter\buckConverterRev2.sch (Sheet: 1/1)

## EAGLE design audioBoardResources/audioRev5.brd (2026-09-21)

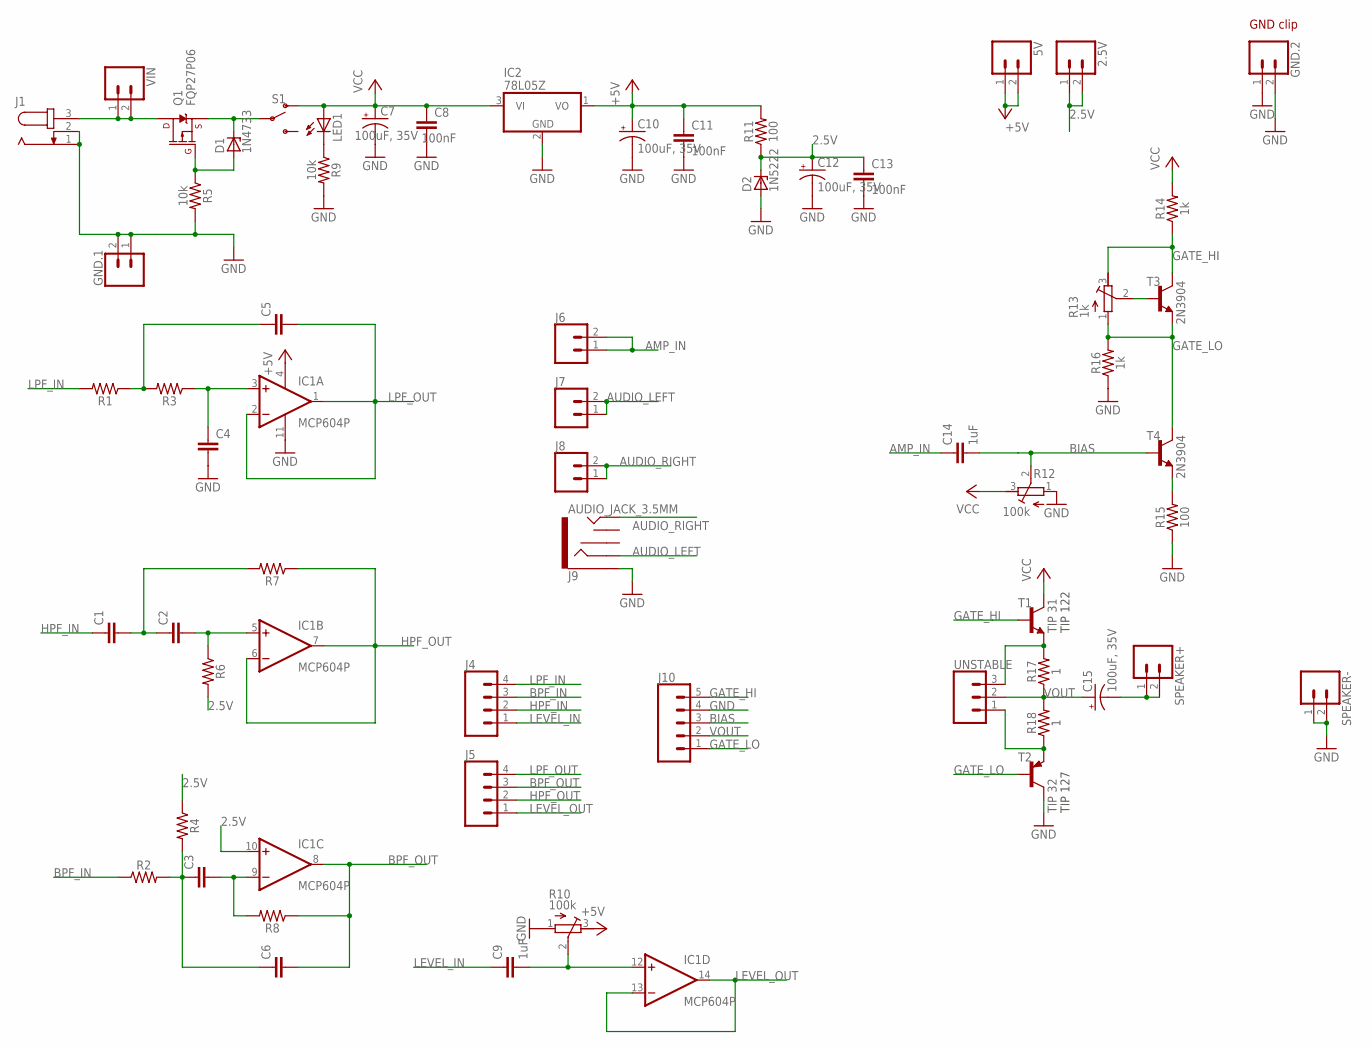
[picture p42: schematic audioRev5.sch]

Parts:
2.5V, 5V: CONN_02; 1X02
C1, C2, C3, C4, C5, C6: C-EU025-025X050; C025-025X050
C7, C10, C12, C15: 100uF, 35V; E2,5-6
C8, C11, C13: 100nF; C025-025X050
C9, C14: 1uF; C025-025X050
D1: 1N4733; DO41Z10
D2: 1N5222; DO34Z7
GND.1, GND.2: CONN_02; 1X02
IC1: MCP604P; DIL14
IC2: 78L05Z; TO92
J1: JACK-PLUG0; SPC4077
J4, J5: CONN_04LOCK_LONGPADS; 1X04_LOCK_LONGPADS
J6, J7, J8: CONN_02; 1X02
J9: AUDIO_JACK_3.5MM; AUDIO-JACK
J10: CONN_05PTH_LONGPADS; 1X05_LONGPADS
LED1: LED5MM
Q1: FQP27P06; TO220V
R1, R2, R3, R4, R6, R7, R8: RESISTORAXIAL-0.3; AXIAL-0.3
R5, R9: 10k; AXIAL-0.3
R10, R12: 100k; RTRIM3296W
R11, R15: 100; AXIAL-0.3
R13: 1k; RTRIM3296W
R14, R16: 1k; AXIAL-0.3
R17, R18: 1; AXIAL-0.3
S1: SWITCH-SPDT-PTH-11.6X4.0MM; SWITCH_SPDT_PTH_11.6X4.0MM
SPEAKER+: CONN_02; 1X02
SPEAKER-: CONN_02; 1X02
T1: TIP 31; TO220V
T2: TIP 32; TO220V
T3, T4: 2N3904; TO92-EBC
UNSTABLE: CONN_03LOCK_LONGPADS; 1X03_LOCK_LONGPADS
VIN: CONN_02; 1X02

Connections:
2.5V: 2.5V.1, 2.5V.2, C12.+, C13.1, D2.C, IC1.10 (+IN), R4.P$1 (1), R6.P$2 (2), R11.P$1 (1)
+5V: 5V.1, 5V.2, C10.+, C11.1, IC1.4 (V+), IC2.1 (VO), R10.3 (E), R11.P$2 (2)
AMP_IN: C14.1, J6.1, J6.2
AUDIO_LEFT: J7.1, J7.2, J9.RING
AUDIO_RIGHT: J8.1, J8.2, J9.TIP
BIAS: C14.2, J10.3, R12.2 (S), T4.B
BPF_IN: J4.3, R2.P$1 (1)
BPF_OUT: C6.2, IC1.8 (OUT), J5.3, R8.P$1 (1)
DRAIN: J1.3, Q1.2 (D), VIN.1, VIN.2
GATE: D1.A, Q1.1 (G), R5.P$1 (1)
GATE_HI: J10.5, R13.3 (E), R14.P$1 (1), T1.1 (B), T3.C
GATE_LO: J10.1, R13.1 (A), R16.P$2 (2), T2.1 (B), T3.E, T4.C
GND: C4.2, C7.-, C8.2, C10.-, C11.2, C12.-, C13.2, D2.A, GND.1.1, GND.1.2, GND.2.1, GND.2.2, IC1.11 (V-), IC2.2 (GND), J1.1, J1.2, J9.SLEEVE, J10.4, R5.P$2 (2), R9.P$2 (2), R10.1 (A), R12.1 (A), R15.P$1 (1), R16.P$1 (1), SPEAKER-.1, SPEAKER-.2, T2.2 (C)
HPF_IN: C1.1, J4.2
HPF_OUT: IC1.6 (-IN), IC1.7 (OUT), J5.2, R7.P$1 (1)
LEVEL_IN: C9.1, J4.1
LEVEL_OUT: IC1.13 (-IN), IC1.14 (OUT), J5.1
LPF_IN: J4.4, R1.P$2 (2)
LPF_OUT: C5.2, IC1.1 (OUT), IC1.2 (-IN), J5.4
unnamed: R18.P$1 (1), T2.3 (E), UNSTABLE.1
unnamed: R17.P$2 (2), T1.3 (E), UNSTABLE.3
unnamed: R15.P$2 (2), T4.E
unnamed: C3.1, C6.1, R2.P$2 (2), R4.P$2 (2)
unnamed: C4.1, IC1.3 (+IN), R3.P$1 (1)
unnamed: C5.1, R1.P$1 (1), R3.P$2 (2)
unnamed: C3.2, IC1.9 (-IN), R8.P$2 (2)
unnamed: C2.2, IC1.5 (+IN), R6.P$1 (1)
unnamed: C1.2, C2.1, R7.P$2 (2)
unnamed: C9.2, IC1.12 (+IN), R10.2 (S)
unnamed: C15.-, SPEAKER+.1, SPEAKER+.2
unnamed: LED1.K (C), R9.P$1 (1)
unnamed: R13.2 (S), T3.B
SOURCE: D1.C, Q1.3 (S), S1.2
VCC: C7.+, C8.1, IC2.3 (VI), LED1.A, R12.3 (E), R14.P$2 (2), S1.1 (O), T1.2 (C)
VOUT: C15.+, J10.2, R17.P$1 (1), R18.P$2 (2), UNSTABLE.2

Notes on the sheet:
GND clip
TIP 122
TIP 127

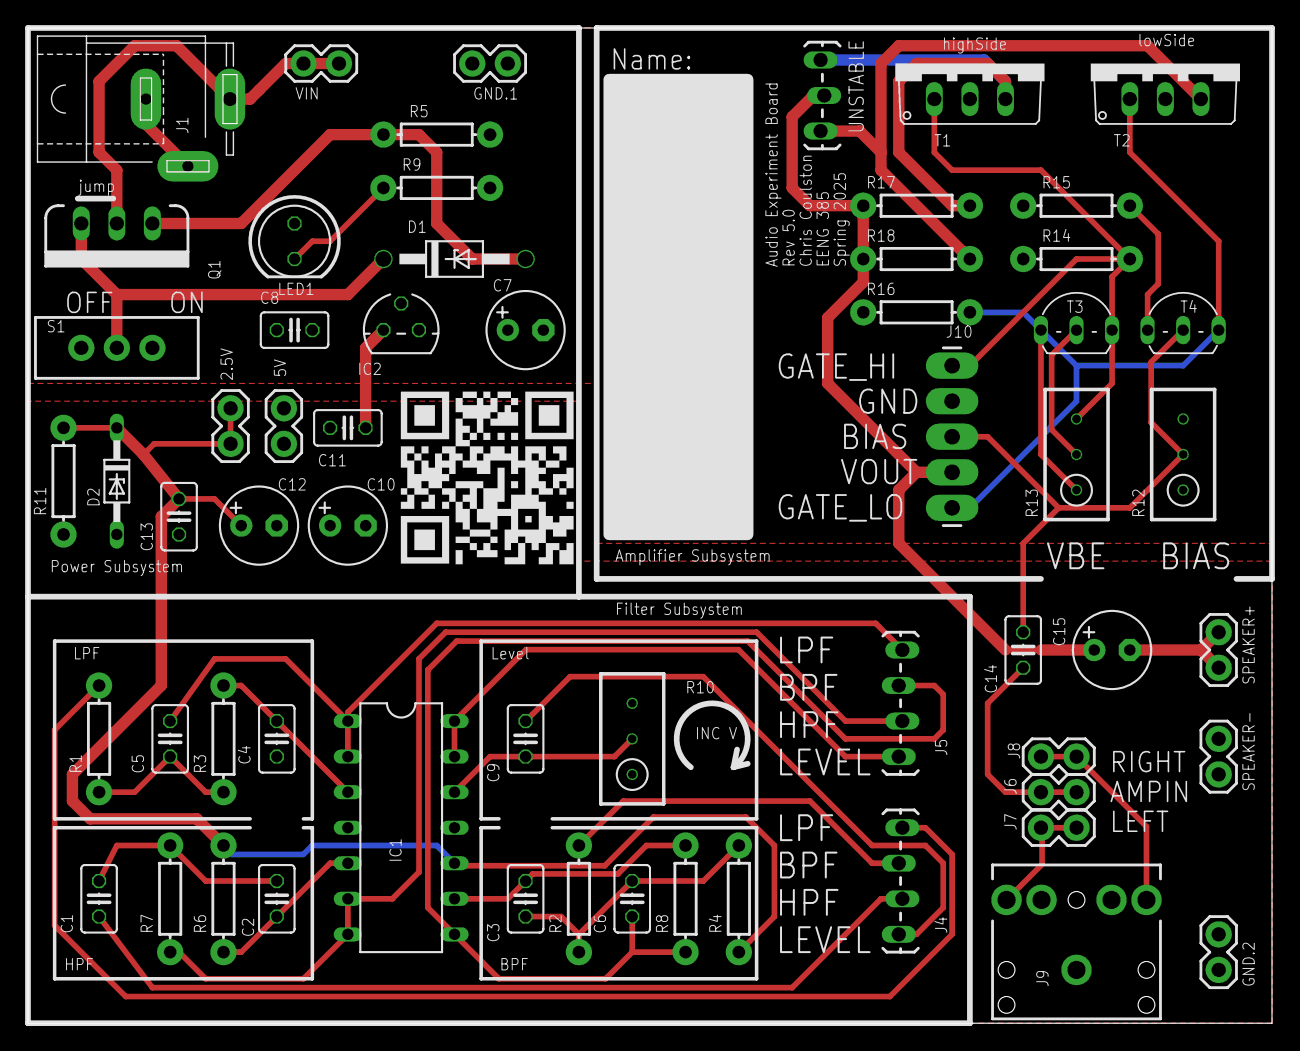
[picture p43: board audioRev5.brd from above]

Board: 2 copper layers, 88.9 x 71.1 mm, 60 parts (0 on the bottom side), 35 nets.

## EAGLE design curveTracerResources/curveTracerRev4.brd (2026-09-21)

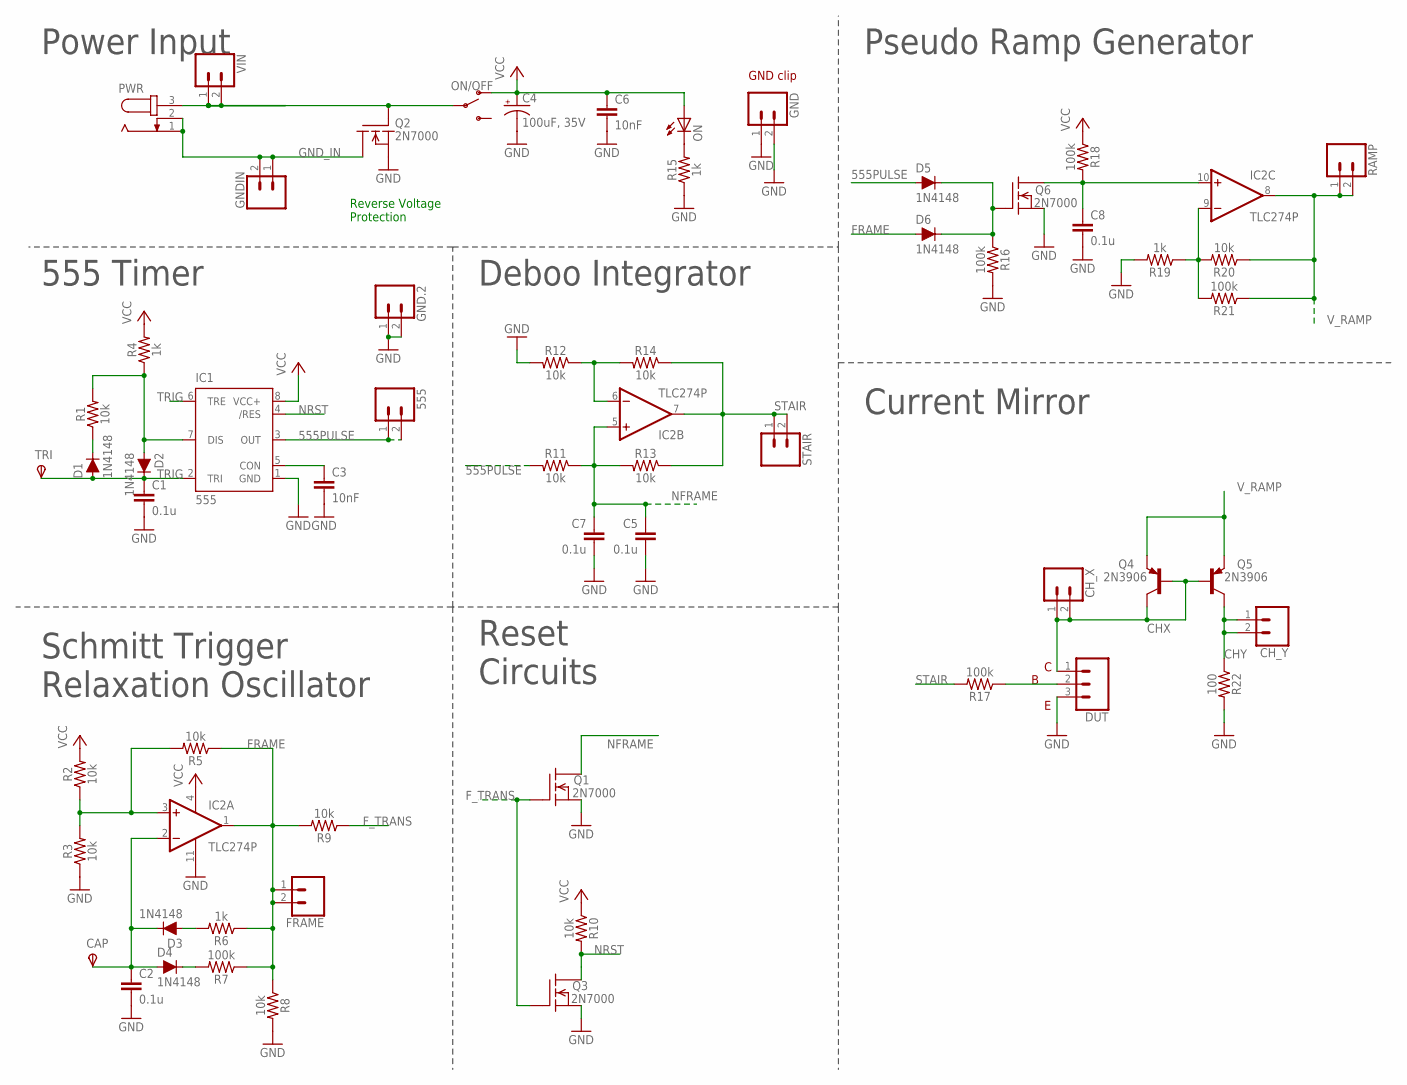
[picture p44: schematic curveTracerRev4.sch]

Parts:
555: CONN_02; 1X02
C1, C2, C5, C7, C8: 0.1u; C050-024X044
C3, C6: 10nF; C050-024X044
C4: 100uF, 35V; E2,5-6
CAP: TPSPAD1-13Y; P1-13Y
CH_X: CONN_02; 1X02
CH_Y: CONN_02; 1X02
D1, D2, D3, D4, D5, D6: 1N4148; DIODE-1N4148
DUT: CONN_03LOCK_LONGPADS; 1X03_LOCK_LONGPADS
FRAME: CONN_02; 1X02
GND, GND.2: CONN_02; 1X02
GNDIN: CONN_02; 1X02
IC1: 555; DIP08
IC2: TLC274P; DIL14
ON: LED5MM
ON/OFF: SWITCH-SPDT-PTH-11.6X4.0MM; SWITCH_SPDT_PTH_11.6X4.0MM
PWR: JACK-PLUG0; SPC4077
Q1, Q2, Q3, Q6: 2N7000; TO-92
Q4, Q5: 2N3906; TO92
R1, R2, R3, R5, R8, R9, R10, R11, R12, R13, R14, R20: 10k; AXIAL-0.3
R4, R6, R15, R19: 1k; AXIAL-0.3
R7, R16, R17, R18, R21: 100k; AXIAL-0.3
R22: 100; AXIAL-0.3
RAMP: CONN_02; 1X02
STAIR: CONN_02; 1X02
TRI: TPSPAD1-13Y; P1-13Y
VIN: CONN_02; 1X02

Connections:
555PULSE: 555.1, 555.2, D5.A, IC1.3 (OUT), R11.P$2 (2)
CHX: CH_X.1, CH_X.2, DUT.1, Q4.1 (C), Q4.2 (B), Q5.2 (B)
CHY: CH_Y.1, CH_Y.2, Q5.1 (C), R22.P$1 (1)
FRAME: D6.A, FRAME.1, FRAME.2, IC2.1 (OUT), R5.P$1 (1), R6.P$1 (1), R7.P$1 (1), R8.P$1 (1), R9.P$2 (2)
F_TRANS: Q1.2 (G), Q3.2 (G), R9.P$1 (1)
GND: C1.2, C2.2, C3.2, C4.-, C5.2, C6.2, C7.2, C8.2, DUT.3, GND.1, GND.2, GND.2.1, GND.2.2, IC1.1 (GND), IC2.11 (V-), Q1.1 (S), Q2.1 (S), Q3.1 (S), Q6.1 (S), R3.P$1 (1), R8.P$2 (2), R12.P$2 (2), R15.P$1 (1), R16.P$2 (2), R19.P$2 (2), R22.P$2 (2)
GND_IN: GNDIN.1, GNDIN.2, PWR.1, PWR.2, Q2.3 (D)
unnamed: ON/OFF.2, PWR.3, Q2.2 (G), VIN.1, VIN.2
unnamed: ON.K (C), R15.P$2 (2)
unnamed: D1.C, R1.P$1 (1)
unnamed: D2.A, IC1.7 (DIS), R1.P$2 (2), R4.P$1 (1)
unnamed: D3.A, R6.P$2 (2)
unnamed: C3.1, IC1.5 (CON)
unnamed: C2.1, CAP.TP, D3.C, D4.A, IC2.2 (-IN)
unnamed: IC2.3 (+IN), R2.P$1 (1), R3.P$2 (2), R5.P$2 (2)
unnamed: D4.C, R7.P$2 (2)
unnamed: D5.C, D6.C, Q6.2 (G), R16.P$1 (1)
unnamed: DUT.2, R17.P$1 (1)
unnamed: IC2.6 (-IN), R12.P$1 (1), R14.P$2 (2)
unnamed: IC2.9 (-IN), R19.P$1 (1), R20.P$2 (2), R21.P$2 (2)
unnamed: C8.1, IC2.10 (+IN), Q6.3 (D), R18.P$2 (2)
NFRAME: C5.1, C7.1, IC2.5 (+IN), Q1.3 (D), R11.P$1 (1), R13.P$2 (2)
NRST: IC1.4 (/RES), Q3.3 (D), R10.P$2 (2)
STAIR: IC2.7 (OUT), R13.P$1 (1), R14.P$1 (1), R17.P$2 (2), STAIR.1, STAIR.2
TRIG: C1.1, D1.A, D2.C, IC1.2 (TRI), IC1.6 (TRE), TRI.TP
VCC: C4.+, C6.1, IC1.8 (VCC+), IC2.4 (V+), ON.A, ON/OFF.1 (O), R2.P$2 (2), R4.P$2 (2), R10.P$1 (1), R18.P$1 (1)
V_RAMP: IC2.8 (OUT), Q4.3 (E), Q5.3 (E), R20.P$1 (1), R21.P$1 (1), RAMP.1, RAMP.2

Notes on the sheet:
GND clip
Power Input
555 Timer
Schmitt Trigger Relaxation Oscillator
Deboo Integrator
Reset Circuits
Pseudo Ramp Generator
Current Mirror
Reverse Voltage Protection

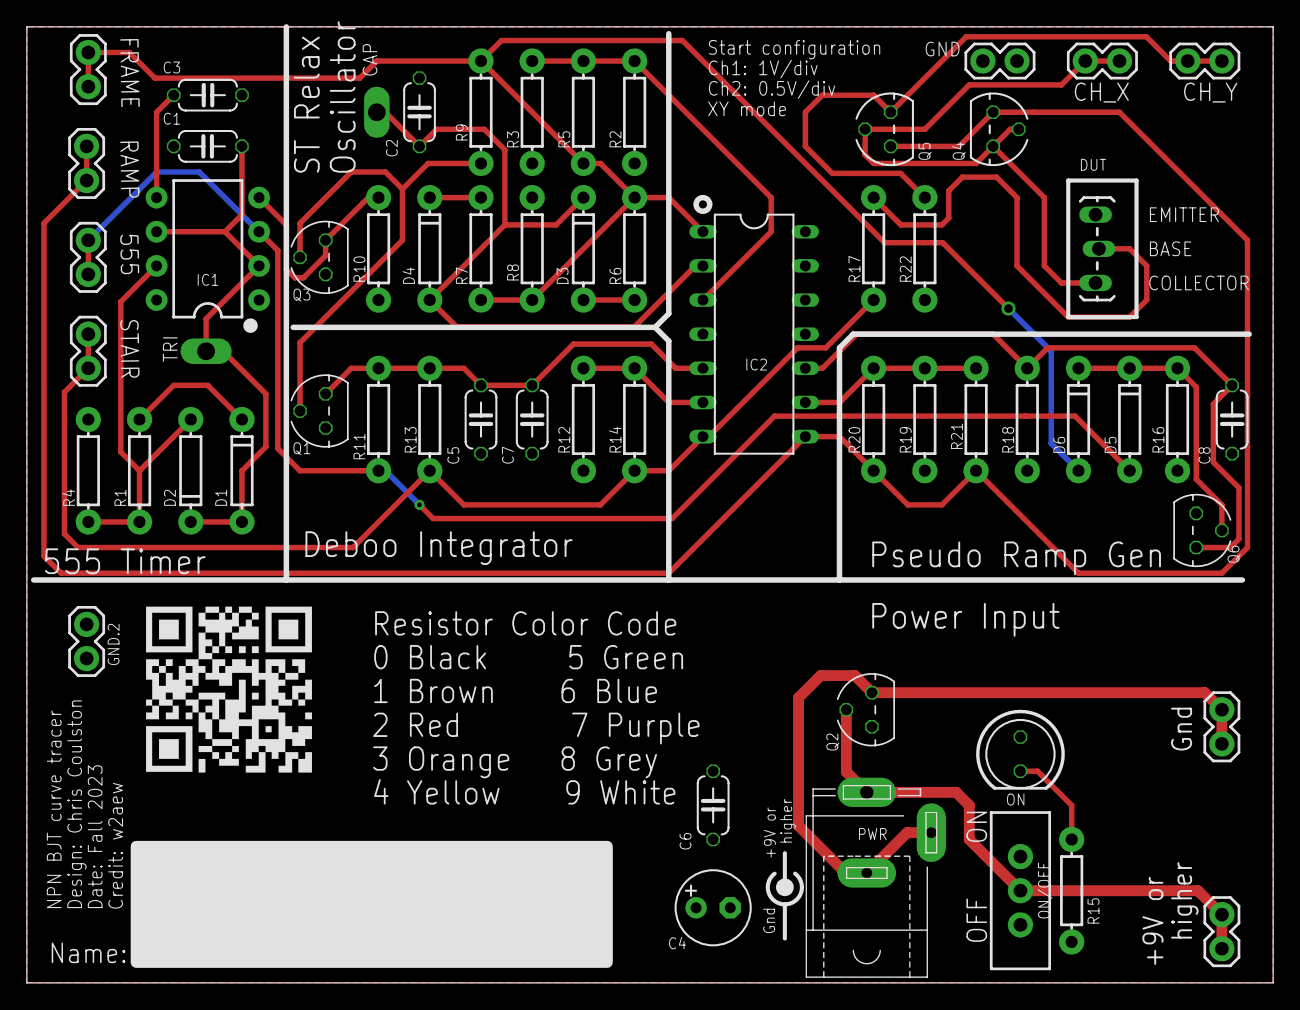
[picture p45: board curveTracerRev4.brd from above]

Board: 2 copper layers, 92.7 x 71.1 mm, 60 parts (0 on the bottom side), 27 nets.

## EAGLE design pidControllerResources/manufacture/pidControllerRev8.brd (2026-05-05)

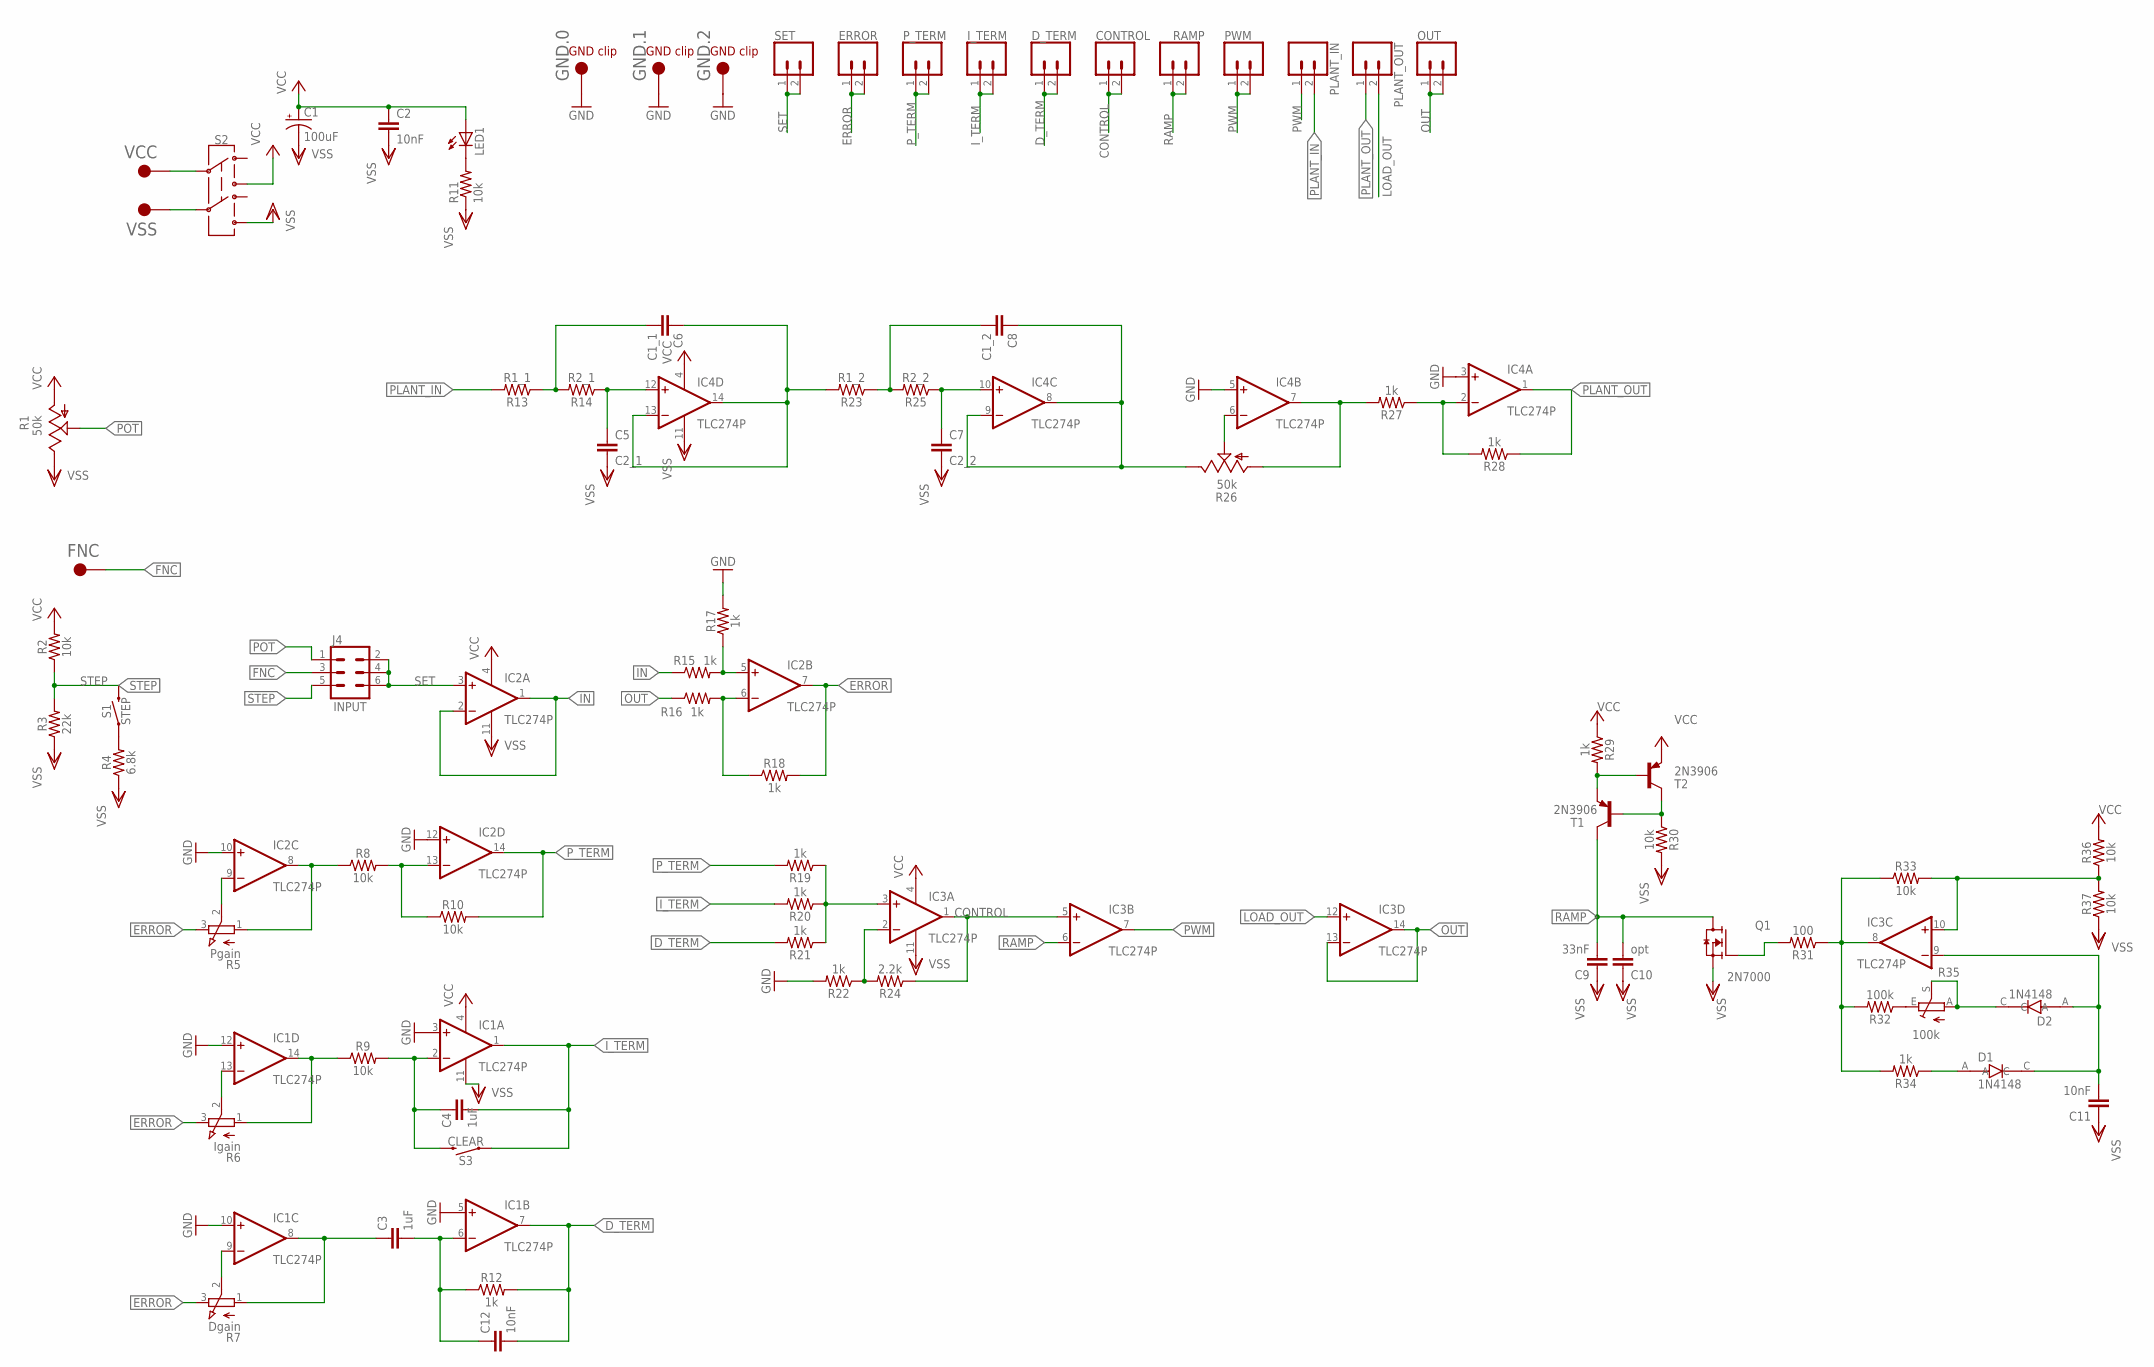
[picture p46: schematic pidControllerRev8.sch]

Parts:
C1: 100uF; SANYO-OSCON_C
C2, C11, C12: 10nF; C1206
C3, C4: 1uF; C1206
C5: C2_1; C1206
C6: C1_1; C1206
C7: C2_2; C1206
C8: C1_2; C1206
C9: 33nF; C1206
C10: opt; C050-024X044
CONTROL: CONN_02LOCK; 1X02_LOCK
D1, D2: 1N4148; SOD2513X120N
D_TERM: CONN_02LOCK; 1X02_LOCK
ERROR: CONN_02LOCK; 1X02_LOCK
FNC: 5016; KEYSTONE_5016
GND.0, GND.1, GND.2: 5016; KEYSTONE_5016
IC1, IC2, IC3, IC4: TLC274P; DIL14
I_TERM: CONN_02LOCK; 1X02_LOCK
J4: INPUT; 2X3
LED1: LEDCHIPLED_1206; CHIPLED_1206
OUT: CONN_02LOCK; 1X02_LOCK
PLANT_IN: CONN_02LOCK; 1X02_LOCK
PLANT_OUT: CONN_02LOCK; 1X02_LOCK
PWM: CONN_02LOCK; 1X02_LOCK
P_TERM: CONN_02LOCK; 1X02_LOCK
Q1: 2N7000; TO92254P458H750-3
R1, R26: 50k; B25P
R2, R8, R9, R10, R30, R33, R36, R37: 10k; 1206
R3: 22k; 1206
R4: 6.8k; 1206
R5: Pgain; EVUF
R6: Igain; EVUF
R7: Dgain; EVUF
R11: 10k; R1206
R12, R15, R16, R17, R18, R19, R20, R21, R22, R27, R28, R29, R34: 1k; 1206
R13: R1_1; 1206
R14: R2_1; 1206
R23: R1_2; 1206
R24: 2.2k; 1206
R25: R2_2; 1206
R31: 100; 1206
R32: 100k; 1206
R35: 100k; S64W
RAMP: CONN_02LOCK; 1X02_LOCK
S1: STEP; TACTILE_SWITCH_SMD_5.2MM
S2: SWITCH-DPDT-SMD-AYZ0202; SWITCH_DPDT_SMD_AYZ0202
S3: CLEAR; TACTILE_SWITCH_SMD_5.2MM
SET: CONN_02LOCK; 1X02_LOCK
T1, T2: 2N3906; TO92-EBC
VCC: 5016; KEYSTONE_5016
VSS: 5016; KEYSTONE_5016

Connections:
CONTROL: CONTROL.1, CONTROL.2, IC3.1 (OUT), IC3.5 (+IN), R24.1
D_TERM: C12.2, D_TERM.1, D_TERM.2, IC1.7 (OUT), R12.2, R21.2
ERROR: ERROR.1, ERROR.2, IC2.7 (OUT), R5.3 (E), R6.3 (E), R7.3 (E), R18.2
FNC: FNC.TP, J4.3
GND: GND.0.TP, GND.1.TP, GND.2.TP, IC1.3 (+IN), IC1.5 (+IN), IC1.10 (+IN), IC1.12 (+IN), IC2.10 (+IN), IC2.12 (+IN), IC4.3 (+IN), IC4.5 (+IN), R17.2, R22.2
IN: IC2.1 (OUT), IC2.2 (-IN), R15.1
I_TERM: C4.2, IC1.1 (OUT), I_TERM.1, I_TERM.2, R20.2, S3.1
LOAD_OUT: IC3.12 (+IN), PLANT_OUT.2
unnamed: IC2.5 (+IN), R15.2, R17.1
unnamed: IC2.6 (-IN), R16.2, R18.1
unnamed: IC4.7 (OUT), R26.A, R27.2
unnamed: C4.1, IC1.2 (-IN), R9.2, S3.3 (2)
unnamed: IC2.8 (OUT), R5.1 (A), R8.1
unnamed: IC3.3 (+IN), R19.1, R20.1, R21.1
unnamed: IC3.2 (-IN), R22.1, R24.2
unnamed: S2.5, VSS.TP
unnamed: IC3.10 (+IN), R33.2, R36.1, R37.2
unnamed: IC4.2 (-IN), R27.1, R28.2
unnamed: IC3.8 (OUT), R31.1, R32.2, R33.1, R34.2
unnamed: R29.2, T1.E, T2.B
unnamed: R30.1, T1.B, T2.C
unnamed: IC1.14 (OUT), R6.1 (A), R9.1
unnamed: S2.2, VCC.TP
unnamed: LED1.C, R11.2
unnamed: C3.1, IC1.8 (OUT), R7.1 (A)
unnamed: IC1.13 (-IN), R6.2 (S)
unnamed: IC2.13 (-IN), R8.2, R10.1
unnamed: R32.1, R35.E
unnamed: IC1.9 (-IN), R7.2 (S)
unnamed: C3.2, C12.1, IC1.6 (-IN), R12.1
unnamed: IC2.9 (-IN), R5.2 (S)
unnamed: R4.2, S1.1
unnamed: C6.2, R13.1, R14.2
unnamed: C5.1, IC4.12 (+IN), R14.1
unnamed: C6.1, IC4.13 (-IN), IC4.14 (OUT), R23.2
unnamed: D1.A, R34.1
unnamed: C8.2, R23.1, R25.2
unnamed: C7.1, IC4.10 (+IN), R25.1
unnamed: C8.1, IC4.8 (OUT), IC4.9 (-IN), R26.E
unnamed: C11.2, D1.C, D2.A, IC3.9 (-IN)
unnamed: IC4.6 (-IN), R26.S
unnamed: Q1.2 (G), R31.2
unnamed: D2.C, R35.A, R35.S
OUT: IC3.13 (-IN), IC3.14 (OUT), OUT.1, OUT.2, R16.1
PLANT_IN: PLANT_IN.2, R13.2
PLANT_OUT: IC4.1 (OUT), PLANT_OUT.1, R28.1
POT: J4.1, R1.S
PWM: IC3.7 (OUT), PLANT_IN.1, PWM.1, PWM.2
P_TERM: IC2.14 (OUT), P_TERM.1, P_TERM.2, R10.2, R19.2
RAMP: C9.2, C10.2, IC3.6 (-IN), Q1.3 (D), RAMP.1, RAMP.2, T1.C
SET: IC2.3 (+IN), J4.2, J4.4, J4.6, SET.1, SET.2
STEP: J4.5, R2.1, R3.2, S1.3 (2)
VCC: C1.+, C2.1, IC1.4 (V+), IC2.4 (V+), IC3.4 (V+), IC4.4 (V+), LED1.A, R1.A, R2.2, R29.1, R36.2, S2.3, T2.E
VSS: C1.-, C2.2, C5.2, C7.2, C9.1, C10.1, C11.1, IC1.11 (V-), IC2.11 (V-), IC3.11 (V-), IC4.11 (V-), Q1.1 (S), R1.E, R3.1, R4.1, R11.1, R30.2, R37.1, S2.6

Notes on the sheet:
GND clip

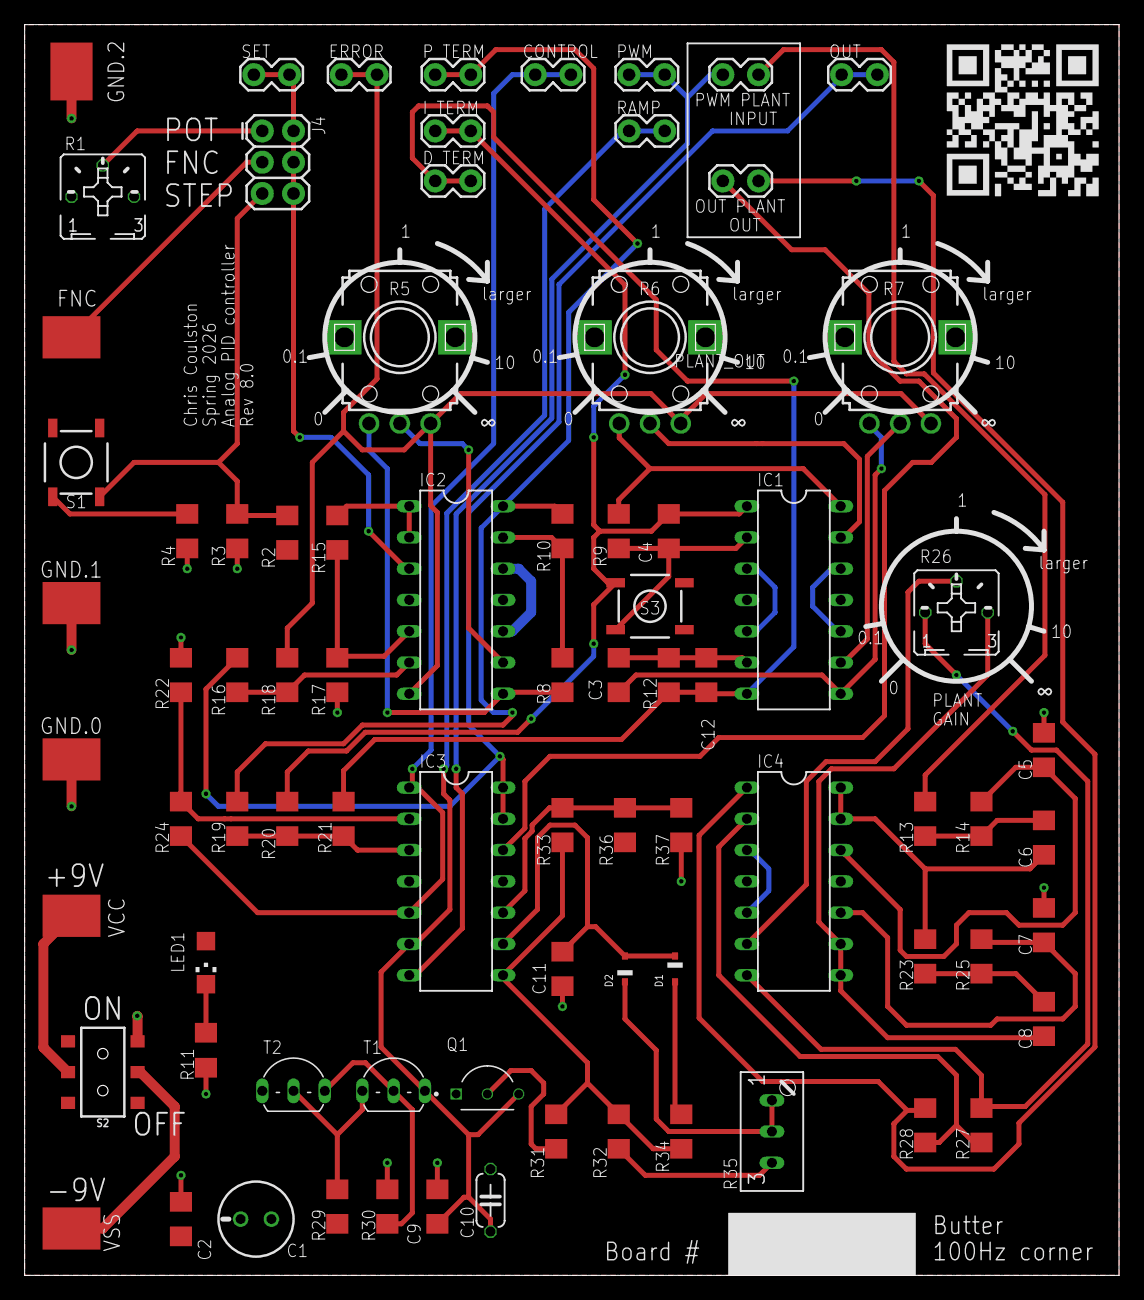
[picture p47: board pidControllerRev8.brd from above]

Board: 2 copper layers, 88.9 x 101.6 mm, 80 parts (0 on the bottom side), 54 nets.

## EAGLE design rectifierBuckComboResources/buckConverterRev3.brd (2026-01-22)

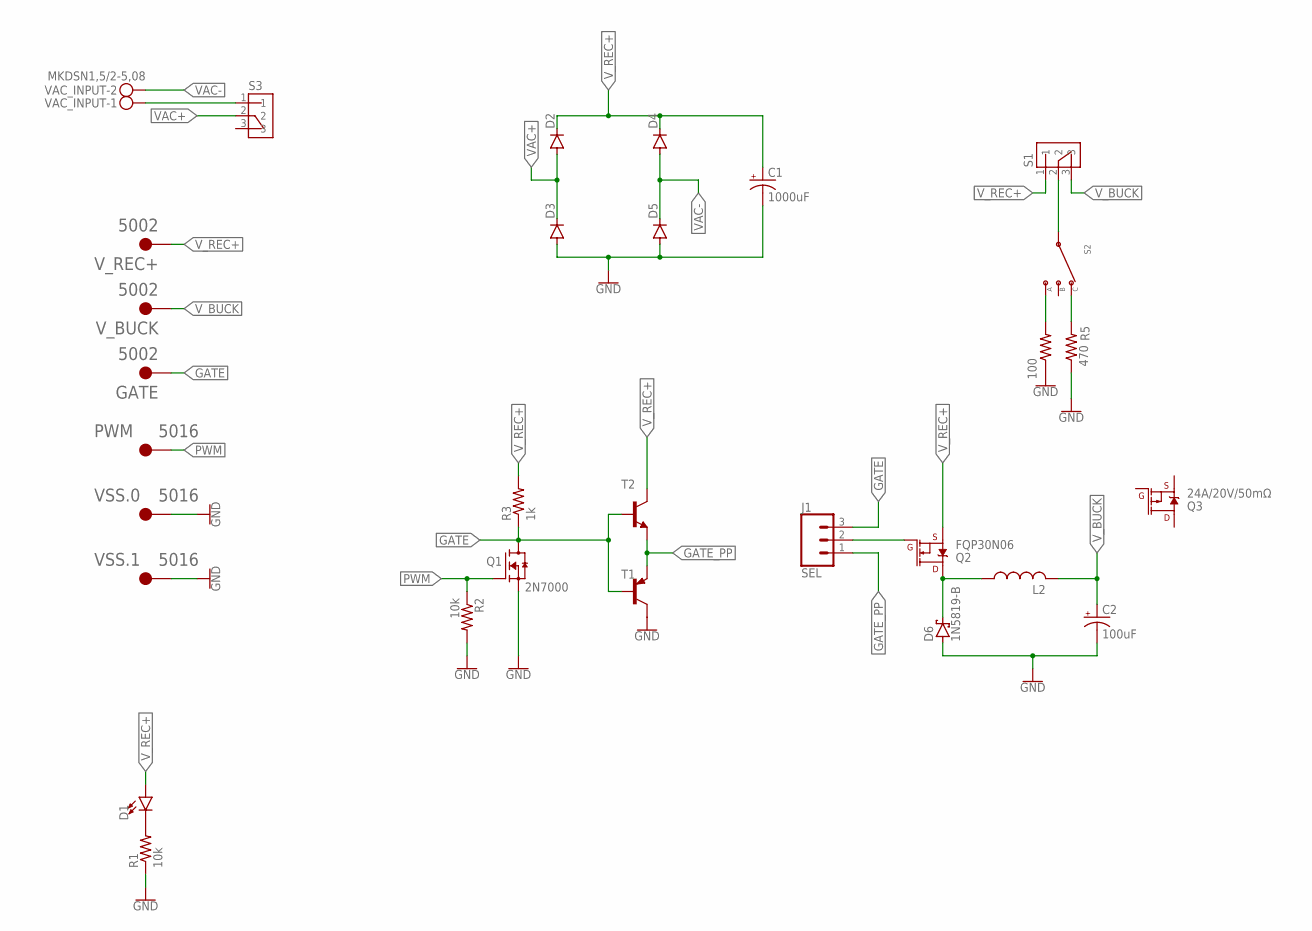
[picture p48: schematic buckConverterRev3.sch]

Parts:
C1: 1000uF; SANYO-OSCON_F13
C2: 100uF; SANYO-OSCON_C
D1: LED5MM; LED_5MM
D2, D3, D4, D5: DIODE-DO41-7.6; DO41-7.6
D6: 1N5819-B; DO41-7.6
GATE: 5002; KEYSTONE_5002
J1: SEL; 1X03_LOCK_LONGPADS
L2: L-US6000-XXX-RC; 6000-XXXX-RC
PWM: 5016; KEYSTONE_5016
Q1: 2N7000; TO92254P458H750-3
Q2: FQP30N06; TO220V
Q3: 24A/20V/50mΩ; TO220V
R1, R2: 10k; 0207/10
R3: 1k; 0207/10
R4: 100; 0617/22
R5: 470; 0309/12
S1: OS102011MS2QN1; SW_OS102011MS2QN1
S2: OS103011MS8QP1; OS102011MS8QP1
S3: ON/OFF; SW_OS102011MS2QN1
T1: 2N3906-PNP-TO92-EBC; TO92-EBC
T2: 2N3904-NPN-TO92-EBC; TO92-EBC
VAC_INPUT: MKDSN1,5/2-5,08
VSS.0, VSS.1: 5016; KEYSTONE_5016
V_BUCK: 5002; KEYSTONE_5002
V_REC+: 5002; KEYSTONE_5002

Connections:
100OHM: R4.2, S2.1
470OHM: R5.2, S2.4 (3)
GATE: GATE.TP, J1.3, Q1.3 (D), R3.1, T1.B, T2.B
GATE_PP: J1.1, T1.E, T2.E
GND: C1.-, C2.-, D3.A, D5.A, D6.A, Q1.1 (S), R1.1, R2.2, R4.1, R5.1, T1.C, VSS.0.TP, VSS.1.TP
unnamed: S3.1, VAC_INPUT.1
unnamed: D1.K (C), R1.2
unnamed: S1.2, S2.2 (C)
unnamed: J1.2, Q2.1 (G)
PWM: PWM.TP, Q1.2 (G), R2.1
SOURCE: D6.C, L2.1, Q2.2 (D)
VAC+: D2.A, D3.C, S3.2
VAC-: D4.A, D5.C, VAC_INPUT.2
V_BUCK: C2.+, L2.2, S1.3, V_BUCK.TP
V_REC+: C1.+, D1.A, D2.C, D4.C, Q2.3 (S), R3.2, S1.1, T2.C, V_REC+.TP

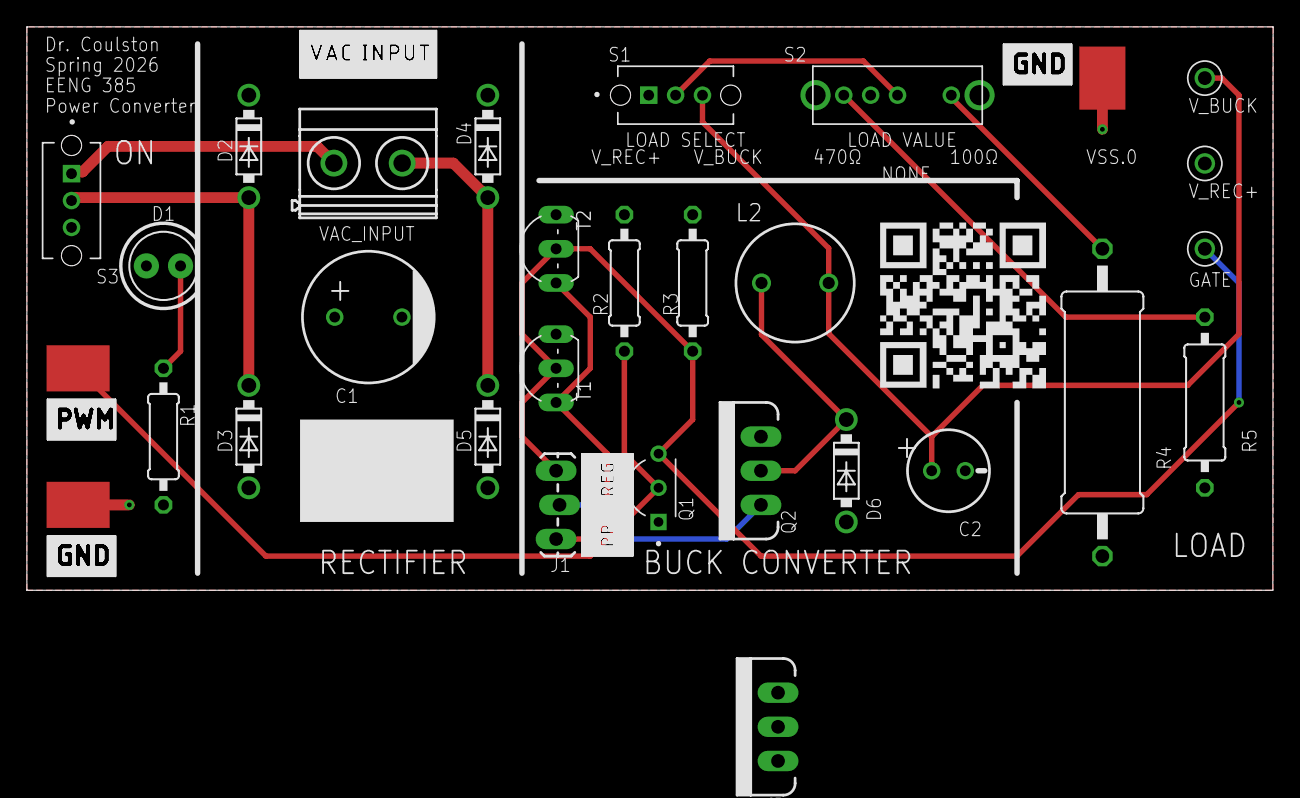
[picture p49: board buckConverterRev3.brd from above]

Board: 2 copper layers, 92.7 x 41.9 mm, 30 parts (0 on the bottom side), 15 nets.

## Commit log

2024-11-20 Initial upload of lab documents
    [EENG 385 Student Lab Section.xlsx, audioBOM.xlsx, audioBoardBehavior.xlsx, audioBoardBehaviorSolved.xlsx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]
2024-12-02 Curve Tracer Labs
    Moved the assembly instructions out of first two labs so that they are less voluminous.
    [audioBOM.xlsx, audioBoardBehaviorSolved.xlsx, current.xlsx, rampVsChargeSolved.xlsx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]
2024-12-02 Create EENG 385 Spring Syllabus.docx
2024-12-03 Formatting and Assembly Guide
    Changed the Heading 1 and 2 formatting for every lab so that PDF will (hopefully) export them in an outline format. Also split off the assembly instructions into a separate document to reduce the pag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
    [EENG 385 Student Lab Section.xlsx, componentsInParallel.xlsx, filterWorkSheetSolved.xlsx]
2024-12-05 Added pcb materials
    Added EGLE CAD files as well as Gerber files for the PCBs and the bill of materials for both board - these need to be double checked.
    [audioBOM.xlsx, audioRev5.brd, audioRev5.sch, curveTracerRev4.brd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]
2024-12-12 added outcomes and objectives
    [curveTracerBOM.xlsx, labMaterialsPerWeek.xlsx]
2025-06-04 Move PCB files to top level
    [audioBOM.xlsx, audioRev5.brd, audioRev5.sch, curveTracerBOM.xlsx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]
2025-11-17 Adding PID Controller Lab
    [labCalculations.xlsx]
2025-11-18 Assembly instructions for PID controller PCB
    [bomRev7.xlsx]
2025-11-18 pid controller lab
    [labCalculations.xlsx]
2025-12-16 Minor changes
    [calculations.xlsx]
2025-12-21 Pushing most recent changes
    To the PID controller lab
    [bomRev7.xlsx]
2025-12-28 updated lab
    [buck.xls]
2025-12-30 workbook updates for spring 26
2026-01-02 Spring 2026 Workbook updates
    Made the master PDF
2026-01-19 Audio board modifications
    Added a bias resistor and emitter degeneration resistors to the audio board and had to edit an annoying amount of material.
2026-01-22 Adding Two PCBs
    Adding the Recifier with Buck and the PID Controller
    [audioBOM.xlsx, audioRev5.brd, audioRev5.sch, buckConverterBOM_JLC.xlsx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]
2026-01-26 Create rectifierWithBuckDocument.pdf
    Getting the Power Supply PCBs and Lab write-up ready. Just need some pictures and to write up all the solutions
2026-03-05 typo fix use the ~~current~~ **voltage** from the previous problem to help you find the [current thru the rstistor]
2026-03-30 Create README.md
    An introduction to the material contained.
2026-03-30 Add CC logos
    I want others to use these materials and adapt them for their use. The CC license lets them know they can do this with confidence.
2026-05-05 Update the file name
    [pidControllerRev8.brd, pidControllerRev8.sch]
2026-05-05 Add manufacturing files
    [pidControllerMaster_BOM.xlsx, pidControllerRev8.brd, pidControllerRev8.sch, pidController_Centroid.xlsx]
2026-05-30 Ltspice Simulation
    The conversion from MultiSim Live to LTSpice means that I needed to re-write all the simulations. They all are done.
    [calculations.xlsx]

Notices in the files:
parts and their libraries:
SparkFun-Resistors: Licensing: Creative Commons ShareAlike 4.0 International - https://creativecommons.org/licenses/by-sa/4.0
